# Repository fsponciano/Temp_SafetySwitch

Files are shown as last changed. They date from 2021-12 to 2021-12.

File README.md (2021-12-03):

# Temperature-controlled safety switch
Francisco S. Ponciano Ojeda
Superradiant Laser Lab, FEMTO-ST, 2021
---

Design of hardware & software for implementation of a temperature-controlled safety switch for use in research laboratories.
The design was carried out with straight-forward considerations that would allow for the desired operation:
- Low-noise voltage supply to avoid affecting measurement noise.
- Output to allow for safe shutdown of critical power supplies that could generate run-away heating.
- Interface with existing temperature monitoring setup (type K thermocouples) in our experiment.
- User-defined set-points for each input channel.
- External reset button for avoiding accidental reactivation of power supplies.
- Small footprint to allow for switch to be easily incorporated into any space limitations.

As we want to have good precision (<10mV) in the reading of analog signals, we have opted to use the (Teensy 4.0 microcontroller)[http://] and the `ADC` library.
This allows for the analog inputs to be configured to read with 12-bit resolution (~800µV) with some averaging that takes advantage of the speed of the Teensy's speed.

---

The repository contains the KiCAD project with the circuit schematics + PCB designs for construction of this switch.
**Note:** The hardware is split into two PCBs: one for the signal inputs (*i.e.* the thermocouples) and one for the power input and outpus (*i.e.* the signal relays).

A BOM is also provided for ease of access to the part numbers of the electronic components used.

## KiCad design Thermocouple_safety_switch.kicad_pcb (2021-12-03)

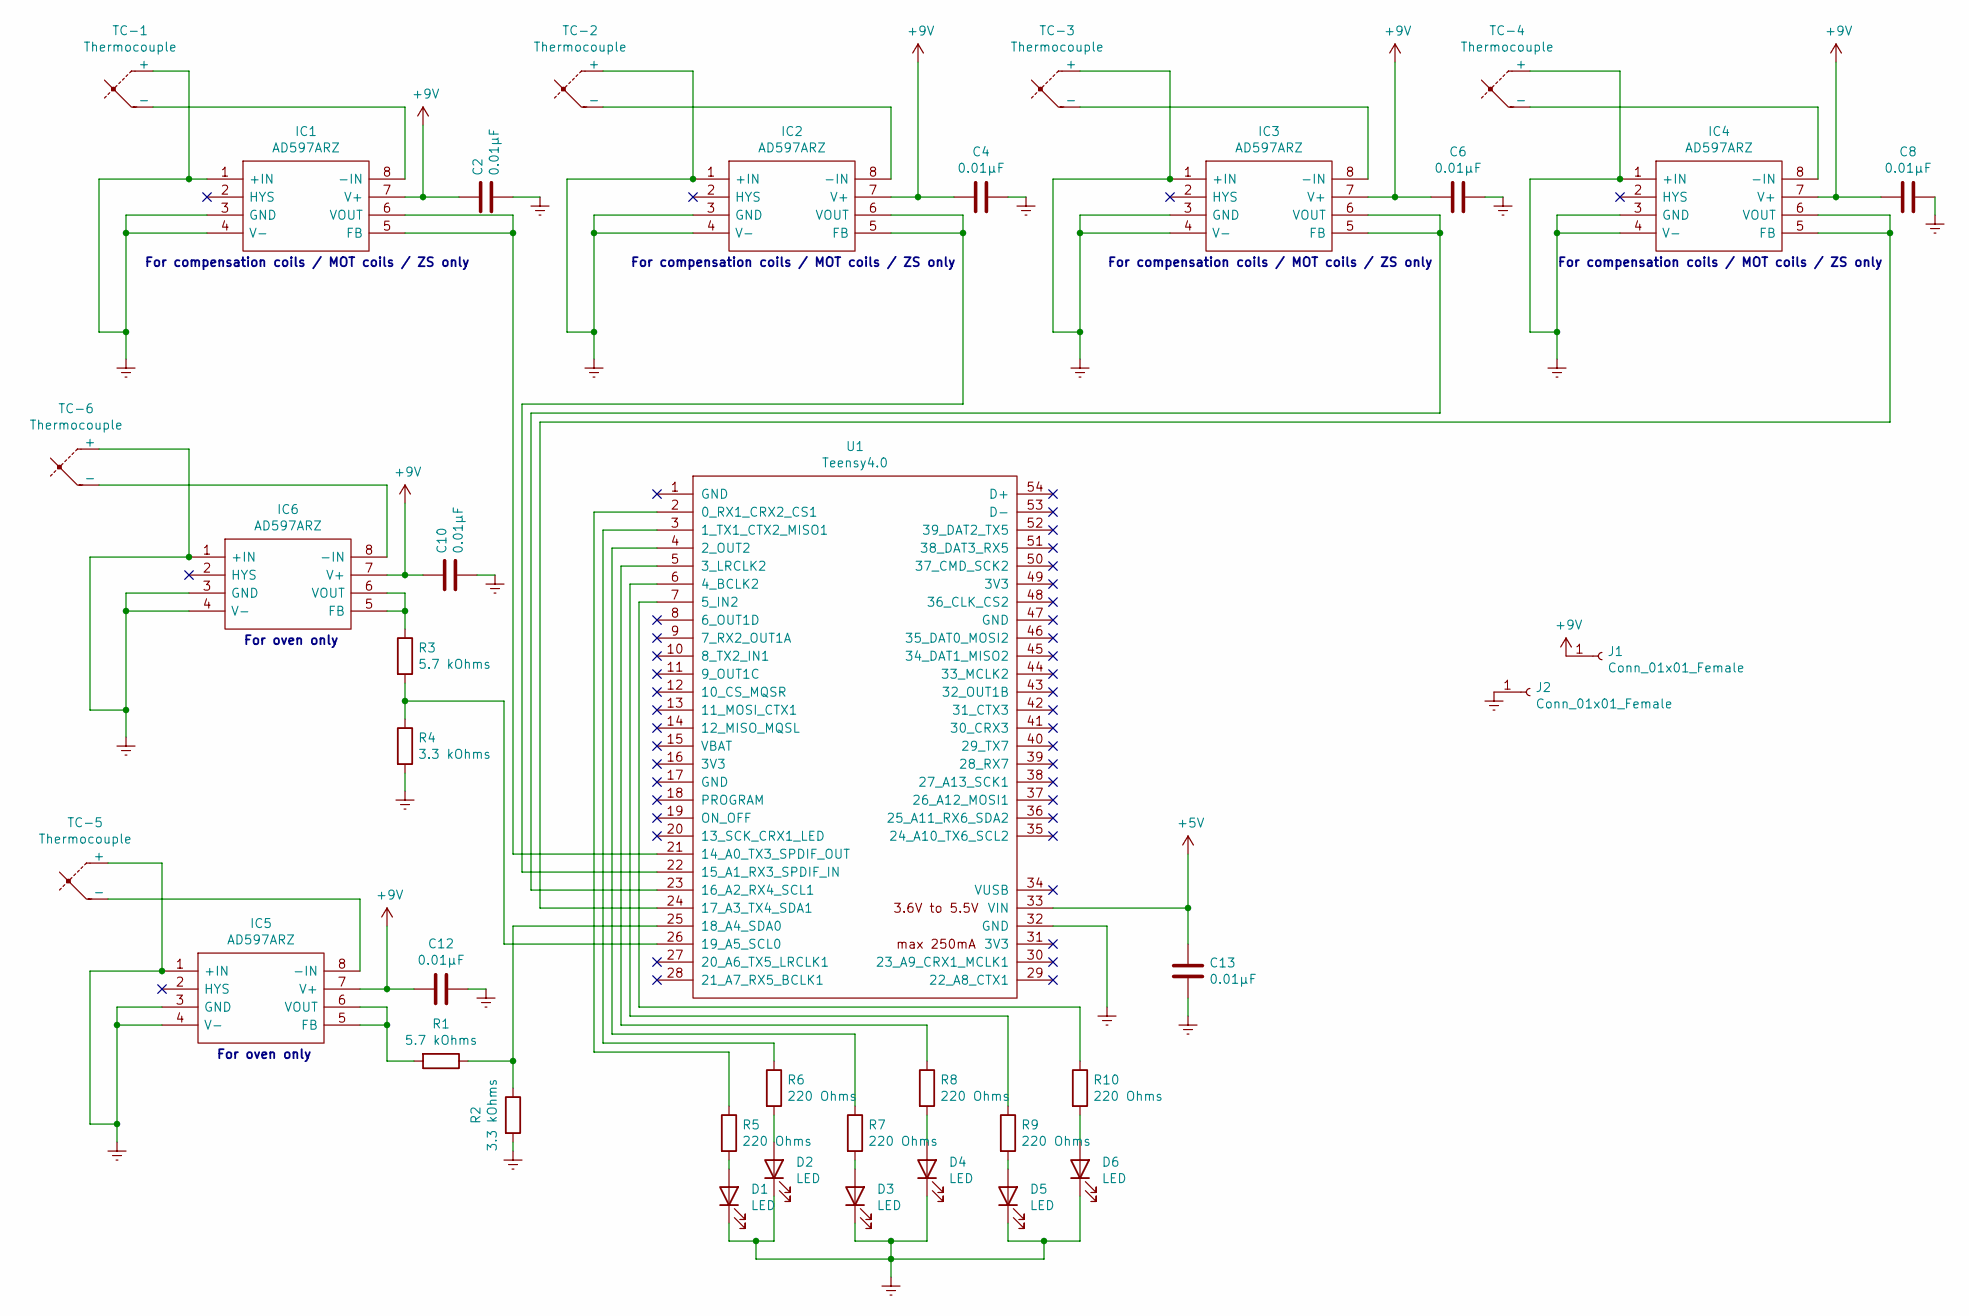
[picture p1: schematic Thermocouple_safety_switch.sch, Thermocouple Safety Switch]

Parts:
C2, C4, C6, C8, C10, C12, C13: 0.01µF; C_0805_2012Metric
D1, D2, D3, D4, D5, D6: LED; LED_D3.0mm
IC1, IC2, IC3, IC4, IC5, IC6: AD597ARZ; SOIC127P600X175-8N; Manufacturer_Part_Number AD597ARZ; Mouser Part Number 584-AD597ARZ
J1, J2: Conn_01x01_Female; SolderWire-2sqmm_1x01_D2mm_OD3.9mm
R1, R3: 5.7 kOhms; R_Axial_DIN0207_L6.3mm_D2.5mm_P10.16mm_Horizontal
R2, R4: 3.3 kOhms; R_Axial_DIN0207_L6.3mm_D2.5mm_P10.16mm_Horizontal
R5, R6, R7, R8, R9, R10: 220 Ohms; R_Axial_DIN0207_L6.3mm_D2.5mm_P10.16mm_Horizontal
TC-1, TC-2, TC-3, TC-4, TC-5, TC-6: Thermocouple; SolderWire-1sqmm_1x02_P5.4mm_D1.4mm_OD2.7mm
U1: Teensy4.0; Teensy40_SMT

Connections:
+5V: C13.1, U1.33 (VIN)
+9V: C2.1, C4.1, C6.1, C8.2, C10.1, C12.1, IC1.7 (V+), IC2.7 (V+), IC3.7 (V+), IC4.7 (V+), IC5.7 (V+), IC6.7 (V+), J1.1
Earth: C2.2, C4.2, C6.2, C8.1, C10.2, C12.2, C13.2, D1.1 (K), D2.1 (K), D3.1 (K), D4.1 (K), D5.1 (K), D6.1 (K), IC1.1 (+IN), IC1.3 (GND), IC1.4 (V-), IC2.1 (+IN), IC2.3 (GND), IC2.4 (V-), IC3.1 (+IN), IC3.3 (GND), IC3.4 (V-), IC4.1 (+IN), IC4.3 (GND), IC4.4 (V-), IC5.1 (+IN), IC5.3 (GND), IC5.4 (V-), IC6.1 (+IN), IC6.3 (GND), IC6.4 (V-), J2.1, R2.2, R4.2, TC-1.1 (+), TC-2.1 (+), TC-3.1 (+), TC-4.1 (+), TC-5.1 (+), TC-6.1 (+), U1.32 (GND)
unnamed: D1.2 (A), R5.2
unnamed: D2.2 (A), R6.2
unnamed: D3.2 (A), R7.2
unnamed: D4.2 (A), R8.2
unnamed: D5.2 (A), R9.2
unnamed: D6.2 (A), R10.2
unnamed: IC1.5 (FB), IC1.6 (VOUT), U1.21 (14_A0_TX3_SPDIF_OUT)
unnamed: IC1.8 (-IN), TC-1.2 (-)
unnamed: IC2.5 (FB), IC2.6 (VOUT), U1.22 (15_A1_RX3_SPDIF_IN)
unnamed: IC2.8 (-IN), TC-2.2 (-)
unnamed: IC3.5 (FB), IC3.6 (VOUT), U1.23 (16_A2_RX4_SCL1)
unnamed: IC3.8 (-IN), TC-3.2 (-)
unnamed: IC4.5 (FB), IC4.6 (VOUT), U1.24 (17_A3_TX4_SDA1)
unnamed: IC4.8 (-IN), TC-4.2 (-)
unnamed: IC5.5 (FB), IC5.6 (VOUT), R1.2
unnamed: IC5.8 (-IN), TC-5.2 (-)
unnamed: IC6.5 (FB), IC6.6 (VOUT), R3.1
unnamed: IC6.8 (-IN), TC-6.2 (-)
unnamed: R1.1, R2.1, U1.25 (18_A4_SDA0)
unnamed: R3.2, R4.1, U1.26 (19_A5_SCL0)
unnamed: R5.1, U1.2 (0_RX1_CRX2_CS1)
unnamed: R6.1, U1.3 (1_TX1_CTX2_MISO1)
unnamed: R7.1, U1.4 (2_OUT2)
unnamed: R8.1, U1.5 (3_LRCLK2)
unnamed: R9.1, U1.6 (4_BCLK2)
unnamed: R10.1, U1.7 (5_IN2)

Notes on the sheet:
For compensation coils / MOT coils / ZS only
For oven only

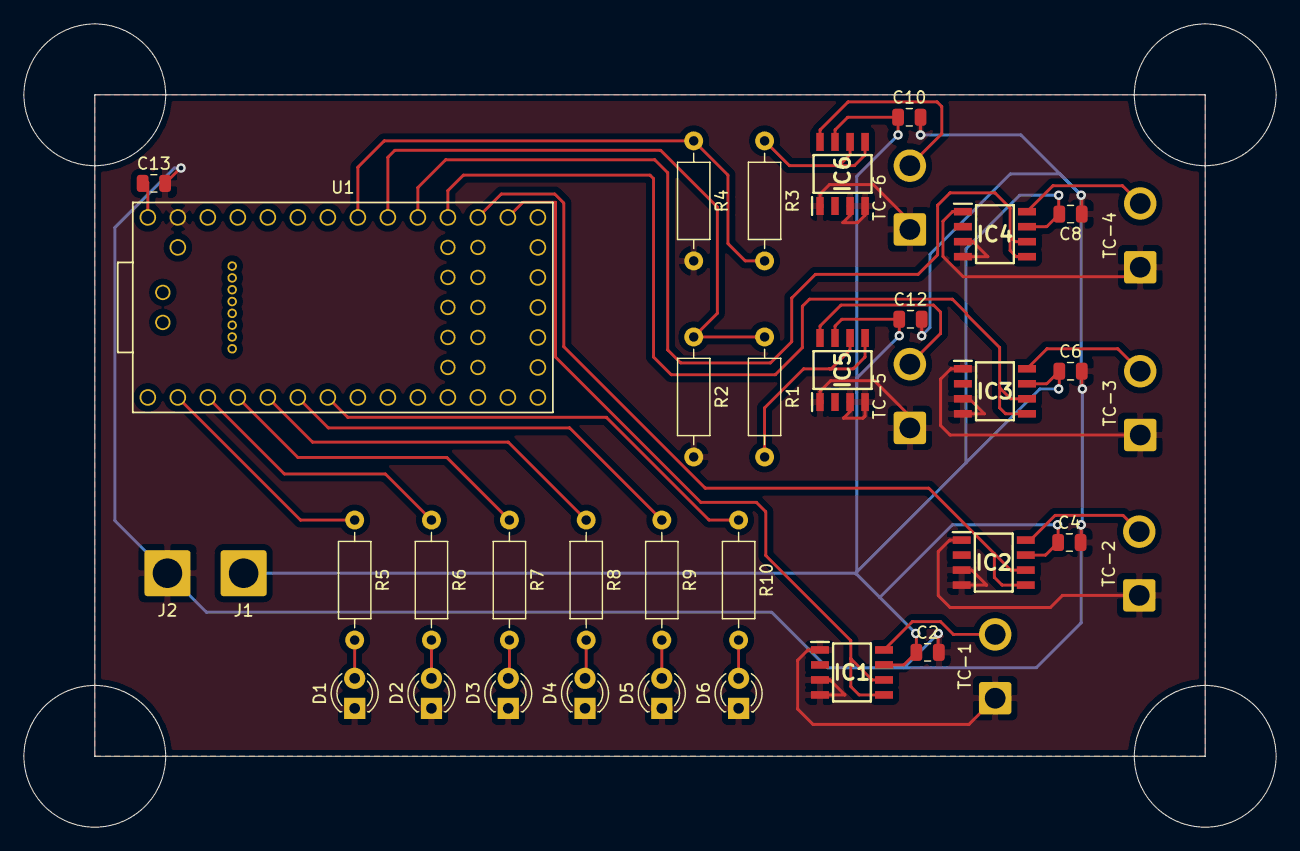
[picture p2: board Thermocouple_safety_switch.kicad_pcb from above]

Board: 2 copper layers, 94.0 x 56.0 mm, 38 parts (0 on the bottom side), 29 nets.

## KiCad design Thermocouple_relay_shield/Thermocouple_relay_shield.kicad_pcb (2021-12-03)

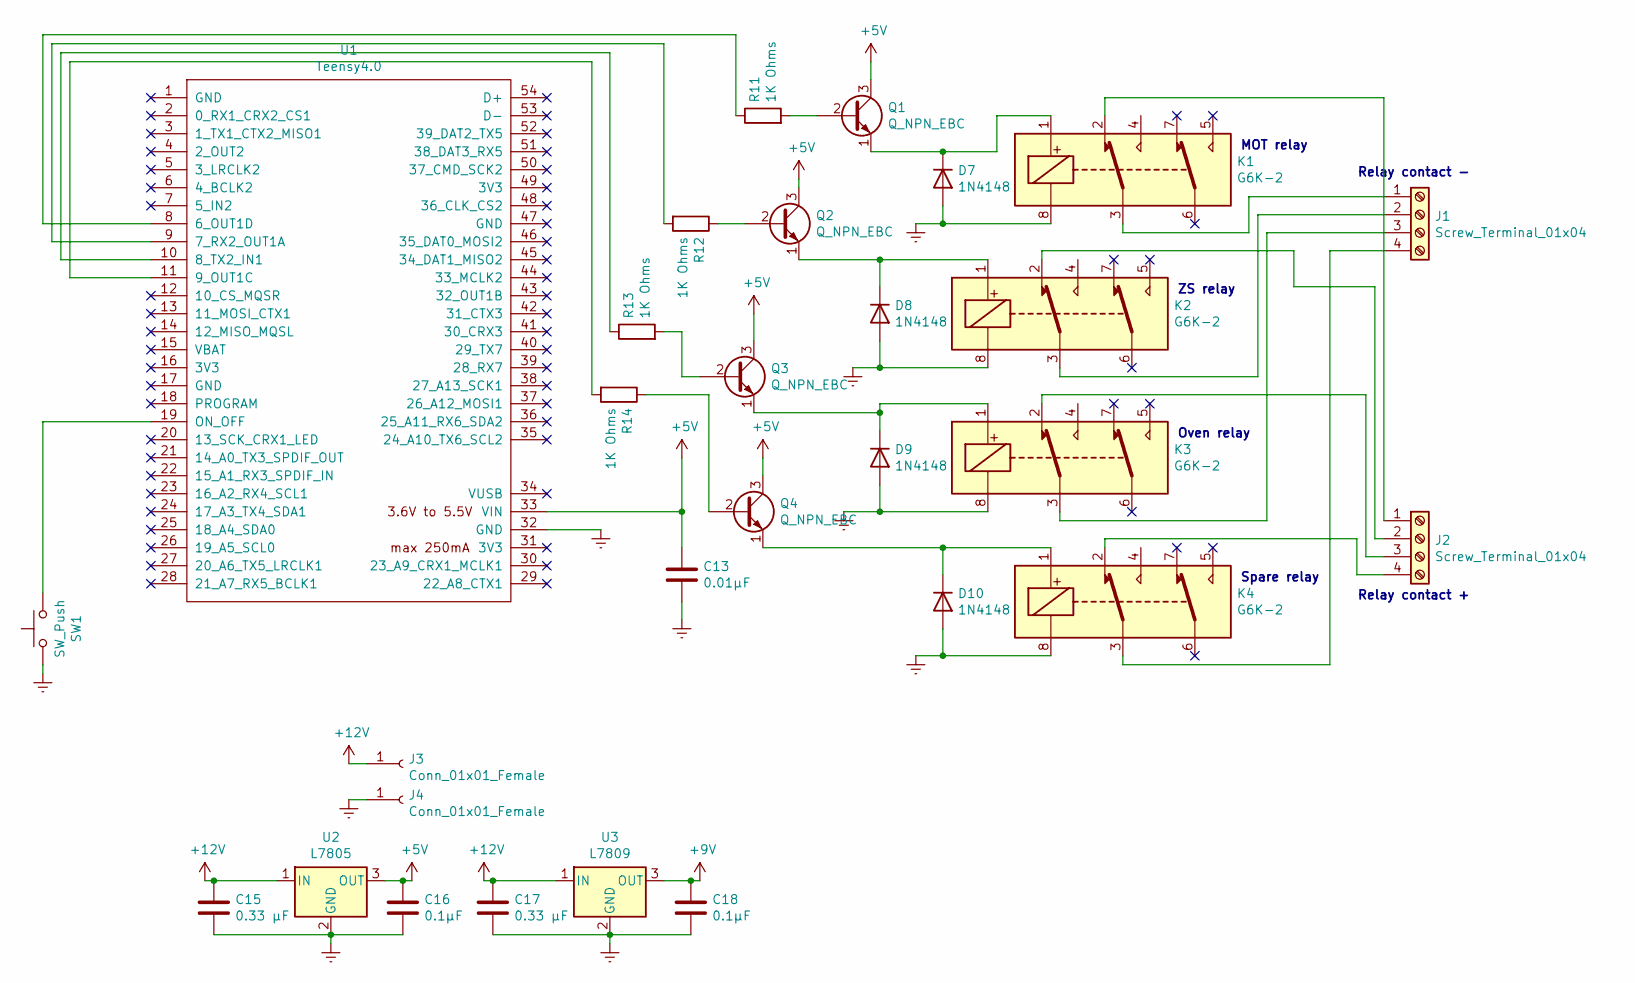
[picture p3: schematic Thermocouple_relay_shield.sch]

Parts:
C13: 0.01µF; C_0805_2012Metric
C15, C17: 0.33 µF; C_0805_2012Metric
C16, C18: 0.1µF; C_0805_2012Metric
D7, D8, D9, D10: 1N4148; D_DO-35_SOD27_P7.62mm_Horizontal
J1, J2: Screw_Terminal_01x04; TerminalBlock_MetzConnect_Type059_RT06304HBWC_1x04_P3.50mm_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
J3, J4: Conn_01x01_Female; SolderWire-2sqmm_1x01_D2mm_OD3.9mm
K1, K2, K3, K4: G6K-2; Relay_DPDT_Omron_G6K-2F-Y
Q1, Q2, Q3, Q4: Q_NPN_EBC; TO-18-3
R11, R12, R13, R14: 1K Ohms; R_Axial_DIN0207_L6.3mm_D2.5mm_P10.16mm_Horizontal
SW1: SW_Push; SolderWire-1sqmm_1x02_P5.4mm_D1.4mm_OD2.7mm
U1: Teensy4.0; Teensy40_SMT
U2: L7805; TO-220-3_Vertical
U3: L7809; TO-220-3_Vertical

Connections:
+5V: C13.1, C16.1, Q1.3 (C), Q2.3 (C), Q3.3 (C), Q4.3 (C), U1.33 (VIN), U2.3 (OUT)
+9V: C18.1, U3.3 (OUT)
+12V: C15.1, C17.1, J3.1, U2.1 (IN), U3.1 (IN)
Earth: C13.2, C15.2, C16.2, C17.2, C18.2, D7.2 (A), D8.2 (A), D9.2 (A), D10.2 (A), J4.1, K1.8, K2.8, K3.8, K4.8, SW1.1, U1.32 (GND), U2.2 (GND), U3.2 (GND)
unnamed: D7.1 (K), K1.1, Q1.1 (E)
unnamed: D8.1 (K), K2.1, Q2.1 (E)
unnamed: D9.1 (K), K3.1, Q3.1 (E)
unnamed: D10.1 (K), K4.1, Q4.1 (E)
unnamed: J1.1, K1.3
unnamed: J1.2, K2.3
unnamed: J1.3, K3.3
unnamed: J1.4, K4.3
unnamed: J2.1, K1.2
unnamed: J2.2, K2.2
unnamed: J2.3, K3.2
unnamed: J2.4, K4.2
unnamed: Q1.2 (B), R11.2
unnamed: Q2.2 (B), R12.1
unnamed: Q3.2 (B), R13.2
unnamed: Q4.2 (B), R14.1
unnamed: R11.1, U1.8 (6_OUT1D)
unnamed: R12.2, U1.9 (7_RX2_OUT1A)
unnamed: R13.1, U1.10 (8_TX2_IN1)
unnamed: R14.2, U1.11 (9_OUT1C)
unnamed: SW1.2, U1.19 (ON_OFF)

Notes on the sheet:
MOT relay
ZS relay
Oven relay
Spare relay
Relay contact -
Relay contact +

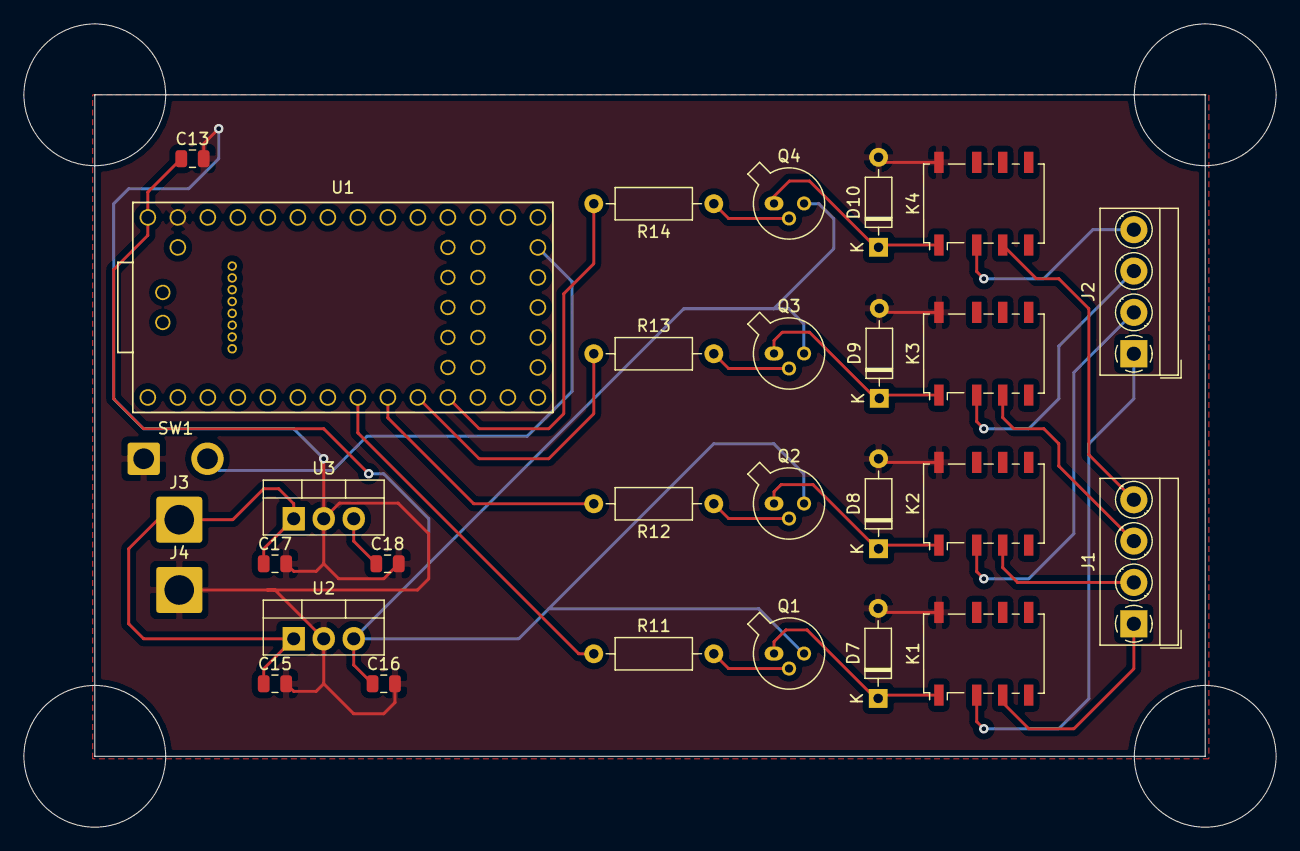
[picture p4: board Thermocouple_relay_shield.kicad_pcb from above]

Board: 2 copper layers, 94.0 x 56.0 mm, 29 parts (0 on the bottom side), 25 nets.

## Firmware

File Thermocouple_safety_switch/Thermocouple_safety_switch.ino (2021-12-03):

#include <ADC.h>
#include <ADC_util.h>

// -- Initialize one ADC for use in the code; Teensy has 2 ADCs that can be used. --
ADC *adc = new ADC();

// -- Define user-friendly variable names: --
const int ZSTherm1 = A0; //Thermocouple for ZS tube.
const int ZSTherm2 = A1; //Thermocouple for ZS MOT side.
const int MOT_Therm1 = A2; //Thermocouple for MOT coils.
// const int Thermocouple4 = A3; //Spare thermocouple - Uncomment if needed.
const int OvenTherm1 = A4; //Thermocouple for oven ONLY.
const int OvenTherm2 = A5; //Thermocouple for oven ONLY.

const int ThermLED1 = 0;
const int ThermLED2 = 1;
const int ThermLED3 = 2;
// const int ThermLED4 = 3; //LED for spare thermocouple - Uncomment if needed.
const int ThermLED5 = 4;
const int ThermLED6 = 5;

const int Relay1 = 6; //ZS power supply.
const int Relay2 = 7; //MOT coils power supply.
const int Relay3 = 8; //Oven supply.
//const int Relay4 = 9; //Spare relay - Uncomment if needed.

const int EmSwitch = 11; //Pin for connecting to emergency stop button in lab.

// - - - - -
// -- Begin main program setup: --
void setup() {

  pinMode(ZSTherm1,INPUT);
  pinMode(ZSTherm2,INPUT);
  pinMode(MOT_Therm1,INPUT);
  // pinMode(Thermocouple4,INPUT); //Pin definition for spare thermocouple - Uncomment if needed.
  pinMode(OvenTherm1,INPUT);
  pinMode(OvenTherm2,INPUT);

  pinMode(ThermLED1,OUTPUT);
  pinMode(ThermLED2,OUTPUT);
  pinMode(ThermLED3,OUTPUT);
  // pinMode(ThermLED4,OUTPUT); //Pin definition for spare thermocouple LED - Uncomment if needed.
  pinMode(ThermLED5,OUTPUT);
  pinMode(ThermLED6,OUTPUT);

  pinMode(Relay1,OUTPUT);
  pinMode(Relay2,OUTPUT);
  pinMode(Relay3,OUTPUT);
  //pinMode(Relay4,OUTPUT); //Spare relay, not currently in use. - Uncomment if needed.

  pinMode(EmSwitch, INPUT_PULLUP); //For connecting Teensy to emergency stop button in lab. Configured as INPUT_PULLUP to allow detection of state of button without interfering in.

  Serial.begin(9600); //Teensy does not care about baud rate.
  Serial.println("Begin setup of safety switch:");

  // Begin configuration of ADC:
  adc->adc0->setReference(ADC_REFERENCE::REF_3V3); //Use internal 3.3V reference on Teensy.
  adc->adc0->setResolution(12); //Hardware limit. 10 bit standard, 12+ bit achieved by averaging.
  adc->adc0->setAveraging(16); //Necessary if we want >10 bit resolutions.
  adc->adc0->setConversionSpeed(ADC_CONVERSION_SPEED::MED_SPEED);
  adc->adc0->setSamplingSpeed(ADC_SAMPLING_SPEED::HIGH_SPEED);

  // The lines below need to be used when changing the resolution of the ADC to ensure proper operation.
  adc->adc0->enableCompare(0.0/3.3*adc->adc0->getMaxValue(), 1); // Measurement will be ready if value > 0.0V.
  adc->adc0->enableCompareRange(0.0*adc->adc0->getMaxValue()/3.3, 3.3*adc->adc0->getMaxValue()/3.3, 1, 1); // Measurement ready if value lies in [0.0,3.3] V.

  Serial.println("Calibrating ...");
  adc->adc0->calibrate();
  adc->adc0->wait_for_cal();
  Serial.println("Calibration OK!");

  if(adc->adc0->fail_flag != ADC_ERROR::CLEAR) {
    Serial.print("ADC0: "); Serial.println(getStringADCError(adc->adc0->fail_flag));
  }

  // Light LED sequence for visual confirmation of completed setup & calibration.
  digitalWrite(ThermLED1,HIGH);
  digitalWrite(ThermLED3,HIGH);
  digitalWrite(ThermLED5,HIGH);
  delay(1000);
  digitalWrite(ThermLED1,LOW);
  digitalWrite(ThermLED3,LOW);
  digitalWrite(ThermLED5,LOW);

  // This should automatically reset the relays that have been previously activated once the Teensy restarts.
  digitalWrite(Relay1,LOW);
  digitalWrite(Relay2,LOW);
  digitalWrite(Relay3,LOW);
  Serial.println("---End setup---");
}

// -- Define variable types for ADC/temperature values: --
int temp_1;
int temp_2;
int temp_3;
// int temp_4; //Uncomment if thermocouple 4 is used.
int temp_5;
int temp_6;
int temp_bkgd; //Offset for taking into account the noise/background on the AD597 signal.

double max_T1 = 30.0; //Max. value of ZS tube temp.
double max_T2 = 30.0; //Max. value of ZS MOT side temp.
double max_T3 = 30.0; //Max. value of MOT coil temp.
// double max_T4 = 30.0; //Max. value of additional input temp. - Uncomment if needed.
double max_T5 = 550.0; //Max. value of oven temp. 1.
double max_T6 = 550.0; //Max. value of oven temp. 2.

// --Define conversion factor for getting ADC->temperature value: --
double t_conv = 3.3/adc->adc0->getMaxValue();

// --Begin main program loop: --
void loop() {

  temp_bkgd = 72;
  //Read the values of the different thermocouples.
  temp_1 = adc->adc0->analogRead(ZSTherm1) - temp_bkgd;
  temp_2 = adc->adc0->analogRead(ZSTherm2);// - temp_bkgd;
  temp_3 = adc->adc0->analogRead(MOT_Therm1) - temp_bkgd;
  // temp_4 = adc->adc0->analogRead(Thermocouple4); //Uncomment if thermocouple 4 is used.
  temp_5 = adc->adc0->analogRead(OvenTherm1);
  temp_6 = adc->adc0->analogRead(OvenTherm2);

  // Uncomment the lines below to observe the ADC reading for a specified thermocouple:
  Serial.println(t_conv / 3.3 * 100,DEC); //Used to check the minimum temperature resolution available on the ADC.
  Serial.print("ADC value (temp. 1): "); Serial.print(temp_1); Serial.print(" - Voltage: "); Serial.print(temp_1 * t_conv / 3.3,DEC); Serial.print(" - Temp.: "); Serial.println((temp_1 * t_conv / 3.3) * 100,DEC);
  Serial.print("ADC value (temp. 2): "); Serial.print(temp_2); Serial.print(" - Voltage: "); Serial.print(temp_2 * t_conv / 3.3,DEC); Serial.print(" - Temp.: "); Serial.println((temp_2 * t_conv / 3.3) * 100,DEC);
  Serial.print("ADC value (temp. 3): "); Serial.print(temp_3); Serial.print(" - Voltage: "); Serial.print(temp_3 * t_conv / 3.3,DEC); Serial.print(" - Temp.: "); Serial.println((temp_3 * t_conv / 3.3) * 100,DEC);
//  Serial.print("ADC value (temp. 4): "); Serial.print(temp_4); Serial.print(" - Voltage: "); Serial.print(temp_4 * t_conv / 3.3,DEC); Serial.print(" - Temp.: "); Serial.println((temp_4 * t_conv / 3.3) * 100,DEC);
//  Serial.print("ADC value (temp. 5): "); Serial.print(temp_5); Serial.print(" - Voltage: "); Serial.println(temp_5 * t_conv / 3.3,DEC);
//  Serial.print("ADC value (temp. 6): "); Serial.print(temp_6); Serial.print(" - Voltage: "); Serial.println(temp_6 * t_conv / 3.3,DEC);
  // * * For reference: ~20 deg C = 275 (ADC) -> 0.26 V; ~30 deg C = 390 (ADC) -> 0.38V (without removing background). * *

  // If the Teensy has an error in reading the values, this allows the message to be checked with the serial monitor.
  if(adc->adc0->fail_flag != ADC_ERROR::CLEAR) {
    Serial.print("ADC0: "); Serial.println(getStringADCError(adc->adc0->fail_flag));
  }

  // The AD597 IC used gives a signal that is proportional to temperature, with the proportionality factor of 10mV/deg. C.
  // We need to divide the setpoint (in deg. C) by a factor of 100 to obtain a value for the signal in mV:
  if(temp_1*t_conv/3.3 > max_T1/100.0 && temp_2*t_conv/3.3 > max_T2/100.0) {
    if(digitalRead(Relay1) == LOW){
      digitalToggle(Relay1);
    } else {
      
    }
    if(temp_1*t_conv > max_T1/100.0) {
      if(digitalRead(ThermLED1) == LOW){
        digitalWrite(ThermLED1,HIGH);
      } else {
        
      }
      Serial.println("Temp. 1 too high!");
    }
    if(temp_2*t_conv > max_T2/100.0) {
      if(digitalRead(ThermLED2) == LOW){
        digitalWrite(ThermLED2,HIGH);
      } else {
        
      }
      Serial.println("Temp. 2 too high!");
    }
  }

  if(temp_3*t_conv/3.3 > max_T3/100.0) {
    if(digitalRead(Relay2) == LOW){
      digitalToggle(Relay2);
    } else {
      
    }
    if(digitalRead(ThermLED3) == LOW){
      digitalToggle(ThermLED3);
    } else {
      
    }
    Serial.println("Temp. 3 too high!");
  }

  // Uncomment the following IF statement when thermocouple 4 is used
  //if(temp_4*t_conv/3.3 > max_T4/100.0) {
  //  digitalToggle(Relay4);
  //  digitalWrite(ThermLED4,HIGH);
  //  Serial.println("Temp. 4 too high!");
  //}

  if(temp_5*t_conv/3.3 > max_T5/100.0 && temp_6*t_conv/3.3 > max_T6/100.0) {
    if(digitalRead(Relay3) == LOW){
      digitalToggle(Relay3);
    } else {
      
    }
    if(temp_5*t_conv > max_T1/100.0) {
      if(digitalRead(ThermLED5) == LOW){
        digitalToggle(ThermLED5);
      } else {
        
      }
      Serial.println("Temp. 5 too high!");
    }
    if(temp_6*t_conv/3.3 > max_T2/100.0) {
      if(digitalRead(ThermLED6) == LOW){
        digitalWrite(ThermLED6,HIGH);
      } else {
        
      }
      Serial.println("Temp. 6 too high!");
    }
  }

  //The behaviour of the push button on the box is as follows:
  // * Holding the button down for 5 seconds will shut off the controller and reset the state of all pins.
  // * After shutting off, pressing the button for 2 seconds will restart the controller.

  // The state of the emergency stop button in the lab can also be read and used to shut off the power supplies:
  if (digitalRead(EmSwitch) == LOW) {
    Serial.println("Everything OK with lab.");
  } else {
    Serial.println("Emergency switch triggered! Shutting down power supplies...");
    if(digitalRead(Relay1) == LOW && digitalRead(Relay2) == LOW && digitalRead(Relay3) == LOW){
      digitalToggle(Relay1);
      digitalToggle(Relay2);
      digitalToggle(Relay3);
      digitalToggle(ThermLED1);
      digitalToggle(ThermLED2);
      digitalToggle(ThermLED3);
      digitalToggle(ThermLED5);
      digitalToggle(ThermLED6);
    //digitalToggle(Relay4);
    } else {
      digitalWrite(Relay1,HIGH);
      digitalWrite(Relay2,HIGH);
      digitalWrite(Relay3,HIGH);
    }
  }
  
  delay(1000); // Value in ms.
}
